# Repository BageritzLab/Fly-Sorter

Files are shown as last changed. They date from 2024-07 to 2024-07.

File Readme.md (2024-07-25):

# Fly Sorter
---
| | |
|-|-|
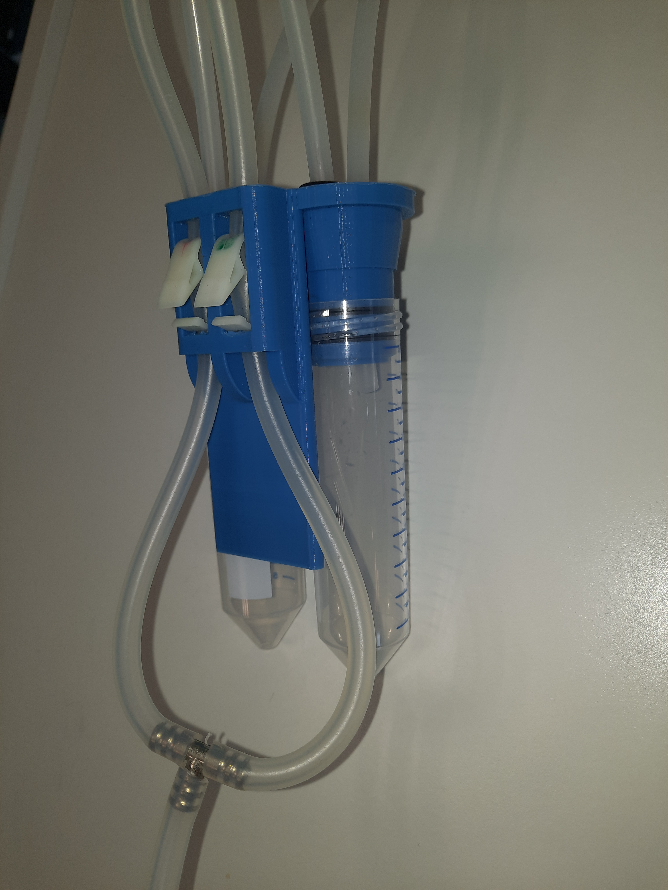
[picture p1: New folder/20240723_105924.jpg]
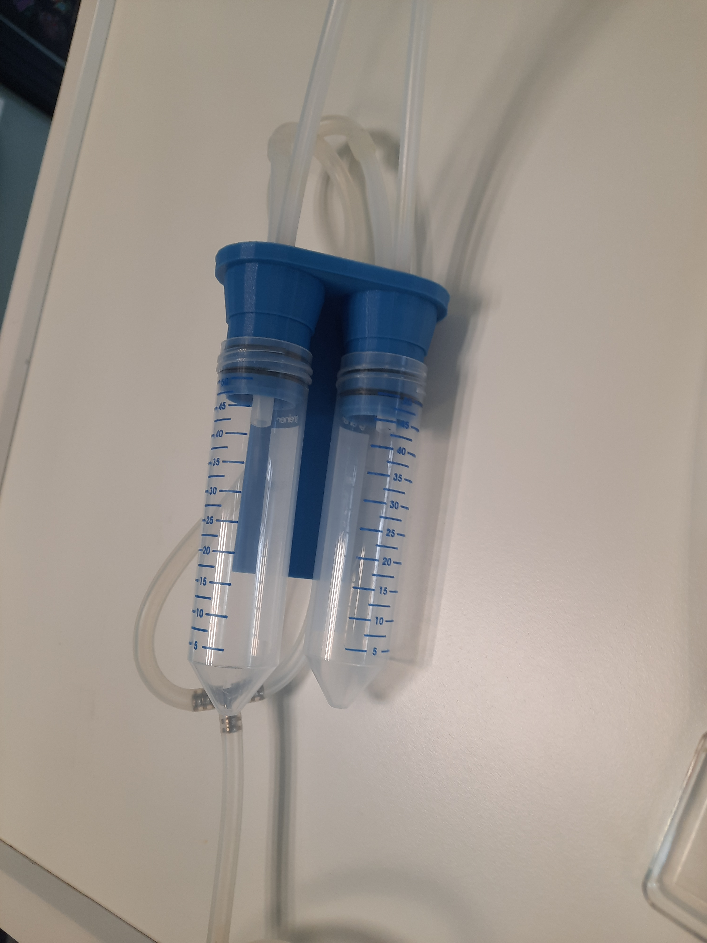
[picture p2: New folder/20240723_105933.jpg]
|| |
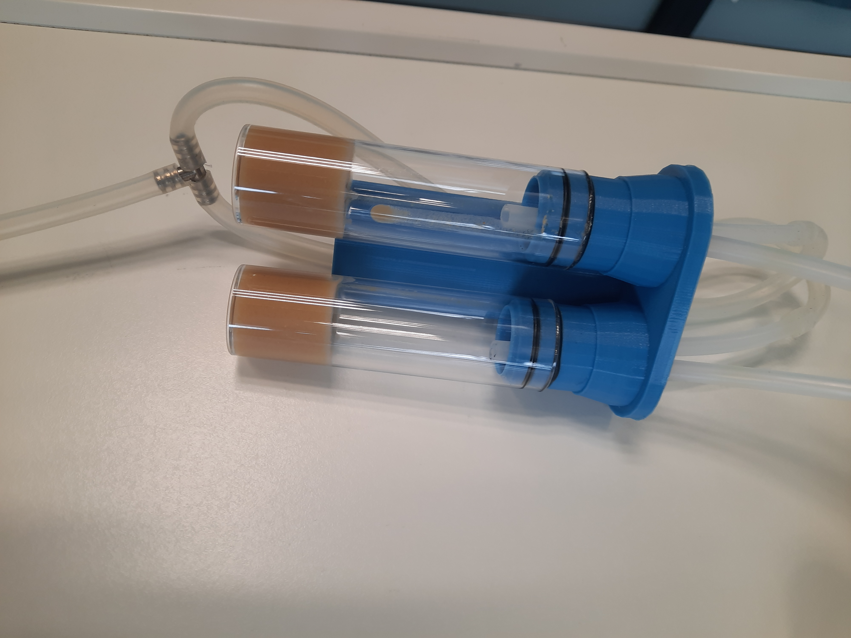
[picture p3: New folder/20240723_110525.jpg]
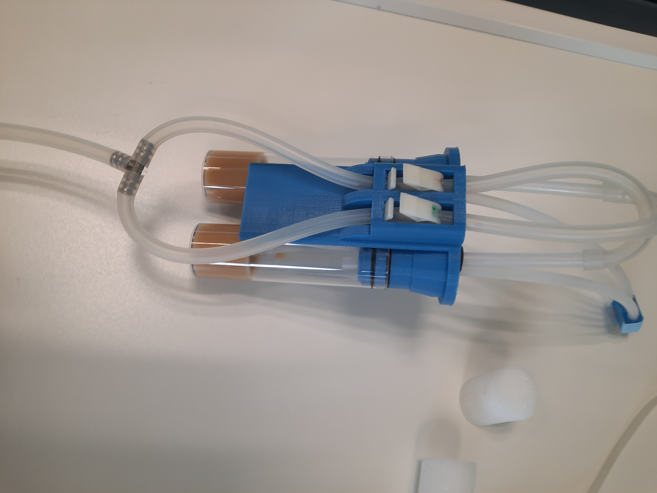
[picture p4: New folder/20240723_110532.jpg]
|||

This is the hand-held Fly Sorter which increases the speed with which *Drosophila* flies can be sorted (e.g. into male and female or by phenotype).

There are two versions of the Fly Sorter:
1. A Quick build that can be made using basic components that can be used with 50 ml Falcon tubes.
2. A 3D printable version that can be used for 50 ml Falcon tubes and standard Laboratpry Fly Vials

Please see the [Building Instructions](https://docs.google.com/document/d/15dwhqNPN-IYihsDtu09y4-i83bKWOhseYIVJSIRqwcc/edit?usp=sharing) for more information.

In our Tests flies that have been sorted 7 consecutive times have not displayed any adverse effects.

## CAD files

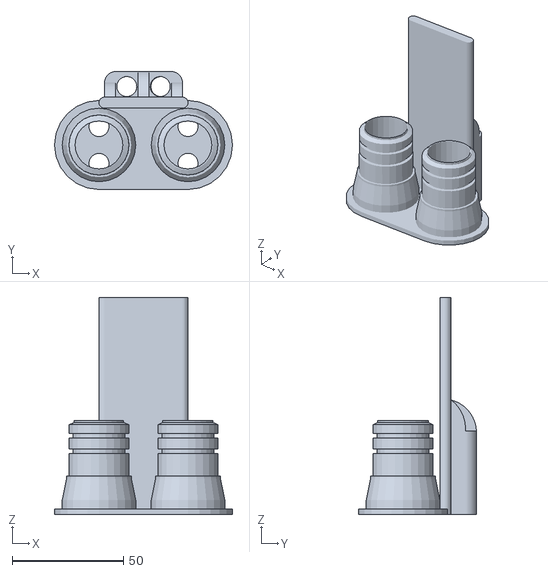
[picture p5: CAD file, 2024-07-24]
Sorter_handle_fly_vials.stl
80.0 x 53.0 x 97.5

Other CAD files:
Sorter_handle_fly_vials.skp

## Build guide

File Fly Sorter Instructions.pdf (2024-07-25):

# Fly Sorter

## Technical Information and Manual

Aim: The Fly Sorter was designed to speed up sorting Drosophila melanogaster flies into categories (e.g. by gender or phenotype) using a handheld vacuum device with 2 chambers.

Quick build (Falcon only) | 1
Material needed: | 1
Building Instructions | 2
3D Printed Device | 6
Material needed: | 6
Build instructions: | 7
How to use the Fly Sorter | 8

# Quick build (Falcon only)

## Material needed:

- 2x 50 ml Falcon Tubes
- 4x silicone cable grommets (inner ø = 6 mm, outer ø = 9 mm)
- A piece of cardboard (~12 cm x ~4 cm)
- Some standard laboratory tape
- T-piece tube connector (ø 5 mm)
- 2x plastic hose clamp
- Drill with 9 mm drill bit Tubing:

- Stiff tubing (inner ø = 4 mm, outer ø = 7 mm)
- 2x ~7 cm
- 2x ~20 cm
- Flexible Tubing (ø = 4 mm, outer ø = 7 mm)
- 2x ~25 cm
- A longer piece to connect to the vacuum

## Building Instructions

1. Drill 2 holes into each of the Falcon Tube caps

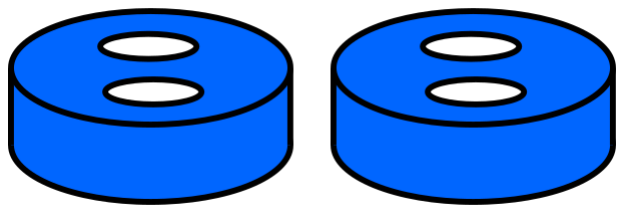
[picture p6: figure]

2. Add the cable grommets into the holes

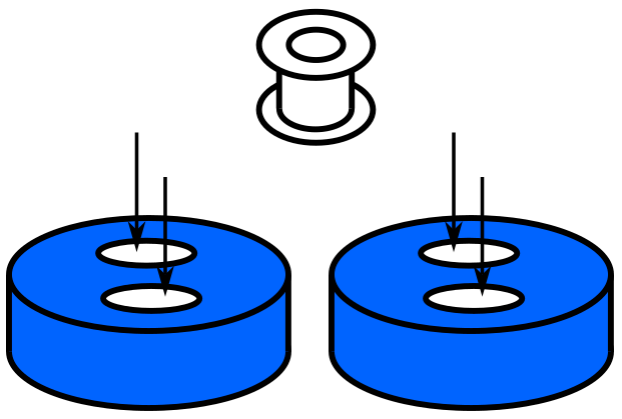
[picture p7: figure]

3. Use tape to fix the lids to each other

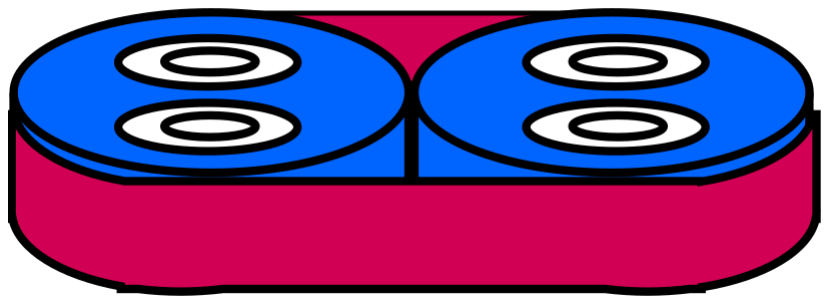
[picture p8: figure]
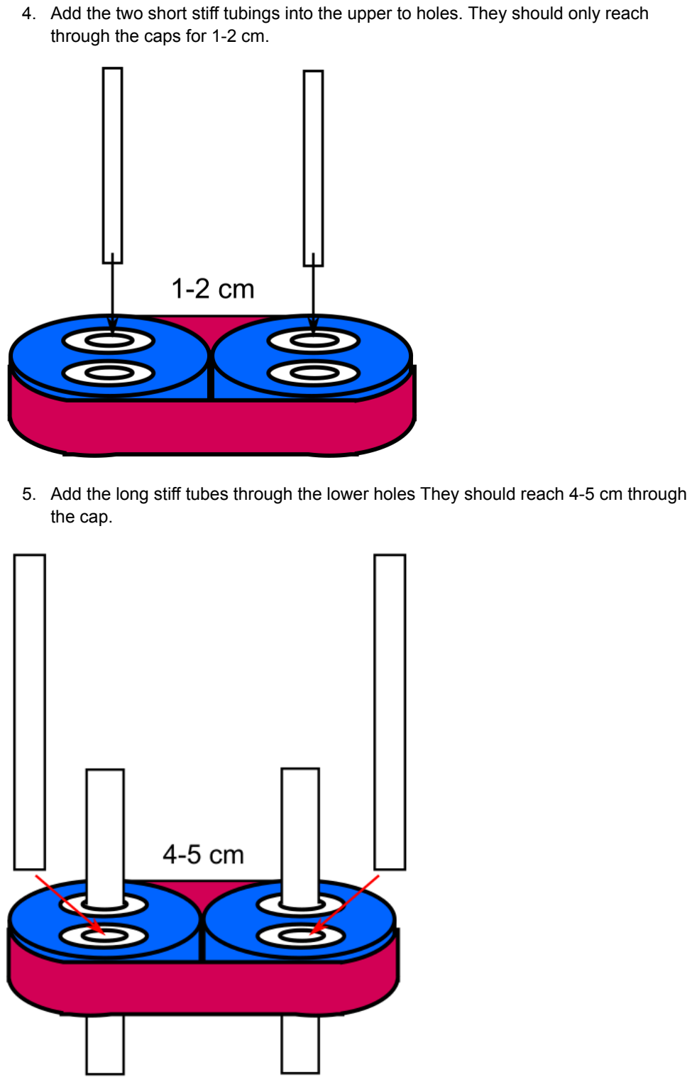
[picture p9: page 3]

4. Add the two short stiff tubings into the upper to holes. They should only reach through the caps for 1-2 cm.
5. Add the long stiff tubes through the lower holes They should reach 4-5 cm through the cap.

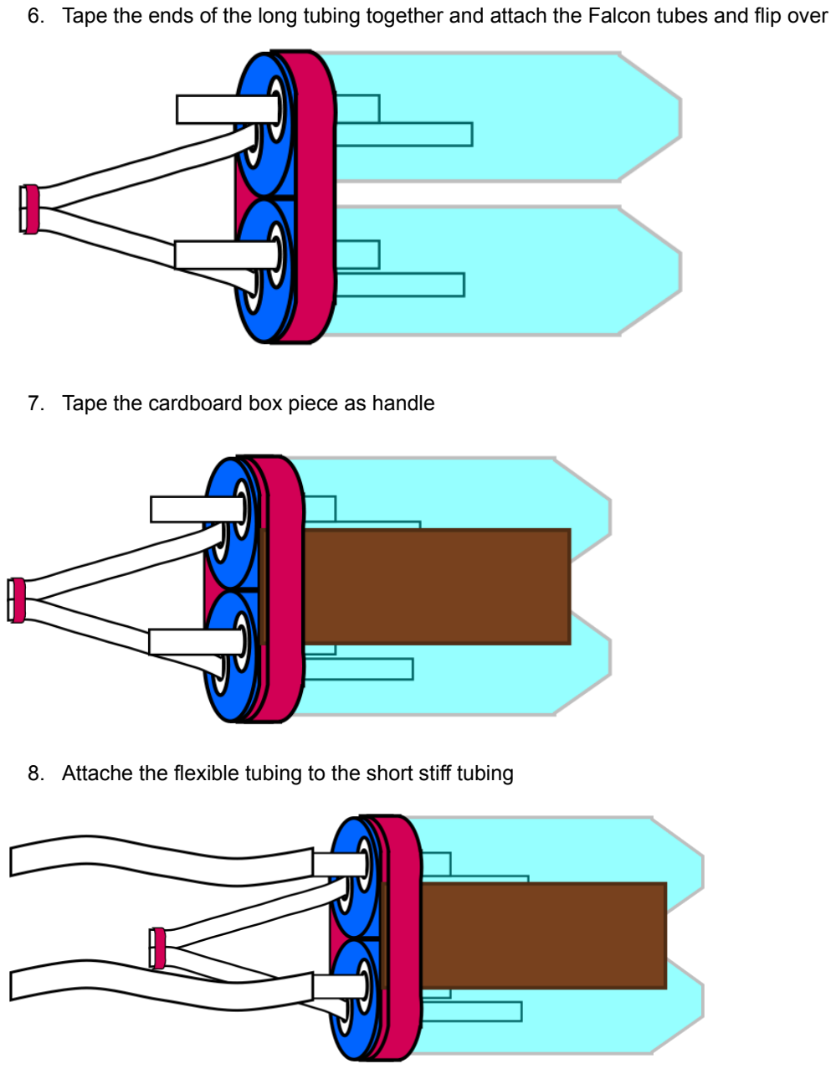
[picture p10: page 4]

6. Tape the ends of the long tubing together and attach the Falcon tubes and flip over
7. Tape the cardboard box piece as handle
8. Attache the flexible tubing to the short stiff tubing

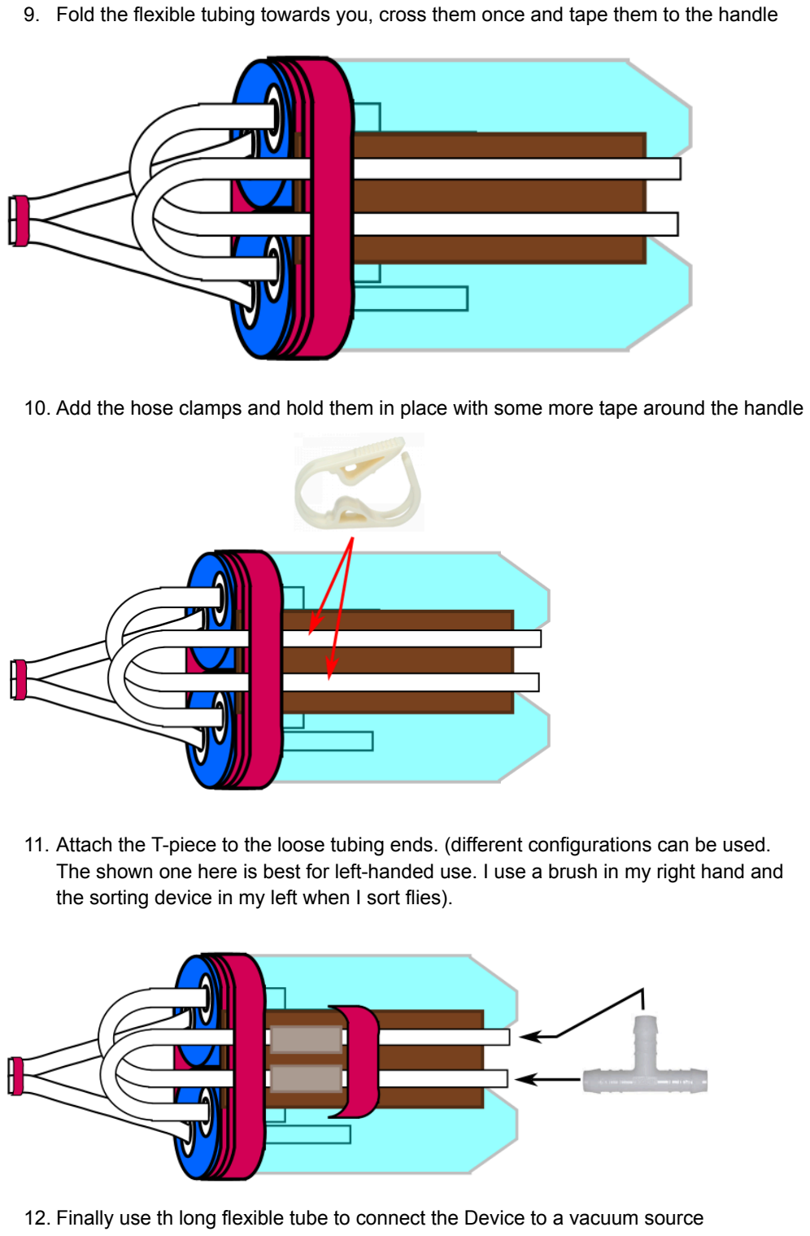
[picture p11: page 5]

9. Fold the flexible tubing towards you, cross them once and tape them to the handle
10. Add the hose clamps and hold them in place with some more tape around the handle
11. Attach the T-piece to the loose tubing ends. (different configurations can be used. The shown one here is best for left-handed use. I use a brush in my right hand and the sorting device in my left when I sort flies).
12. Finally use th long flexible tube to connect the Device to a vacuum source

# 3D Printed Version (Falcons and Fly tubes)

If you have access to a 3D printer I have prepared a 3D printable handle that allows the attachment of Falcon Tubes and standard laboratory fly tubes (inner ø ~27 mm)

## Material needed:

You can download the 3D printer file as .stl from the Bageritz Lab Github page: https://github.com/BageritzLab/Fly-Sorter
I designed the handle in Sketchup Web so an additional .skp is provided.
- 4x silicone cable grommets (inner ø = 6 mm, outer ø = 9 mm)
- T-piece tube connector (ø 5 mm)
- 2x plastic hose clamp
- 4x silicone sealing o-ring (inner ø = 23 mm, outer ø = 27 mm, 2 mm width) Tubing:
- Stiff tubing (inner ø = 4 mm, outer ø = 7 mm)
- 2x ~7 cm
- 2x ~20 cm
- Flexible Tubing (ø = 4 mm, outer ø = 7 mm)
- 2x ~25 cm
- A longer piece to connect to the vacuum

## Build instructions:

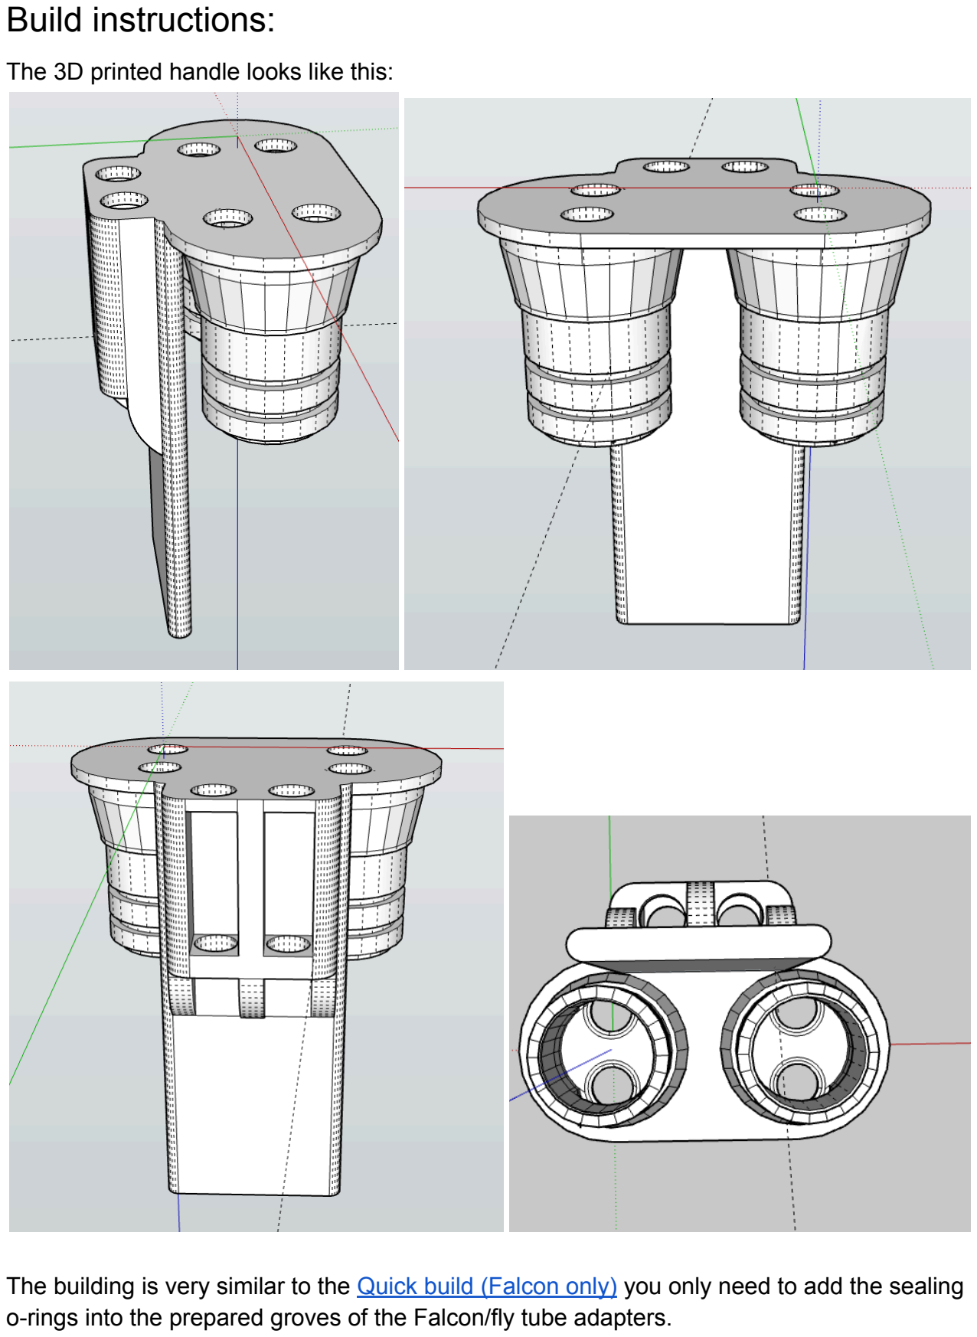
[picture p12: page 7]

The 3D printed handle looks like this:

The building is very similar to the Quick build (Falcon only) you only need to add the sealing o-rings into the prepared groves of the Falcon/fly tube adapters.

# How to use the Fly Sorter

General Use:
1. Attach the Fly Sorter to a vacuum source.
2. (Standby Mode) Adjust the vacuum to the point that a fly that is placed directly in front of the entry is not sucked in but a fly that is already inside of the tubing gets sucked into the collection vial.
(This is important to prevent sucking flies into the wrong vial by accident.)

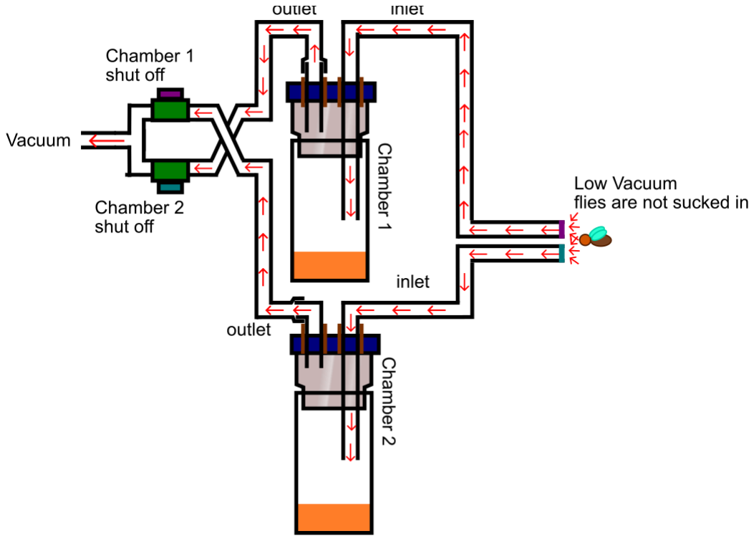
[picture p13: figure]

3. (Active Mode) If you now press the right hose clamp the left collection tube gets shut off and the vacuum in the right collection tube increases to the point were a fly gets sucked into the collection vial and vice versa.

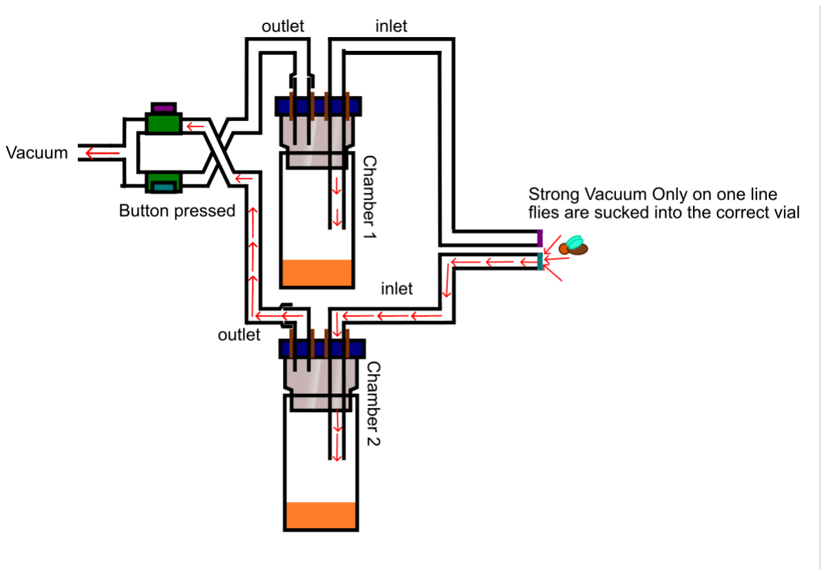
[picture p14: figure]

## Sorting Flies in practice:

I put the flies onto a CO2 pad to anesthezise them. Them I use a bush in the right hand to investigate the flies (decide if they are male of female). The Fly Sorter is held in Standby Mode in the left hand. When we have identified a fly I switch to active Mode by pressing the appropriate button and holding the entry point close to the fly so it is sucked up. This way the CO2 time for the flies is minimized.

Alternatively, you can sort the flies into males and females and put them into distinct piles on the CO2 pad. Then use the Fly Sorter in Active Mode to collect the whole pile.

# Words of caution:

It is possible that eggs get stuck to the tubing and remain there until being dislodged by a following fly. Therefore , there is a risk of contamination. If you are using specific strains that you need to keep separate make sure to rinse the tubing with ethanol/water, and completely dry them.
Alternatively use a new fly sorting setup for each clonal line.

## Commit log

2024-07-23 Adds the sorter handles for fly tubes
    [Sorter_handle_fly_vials.skp, Sorter_handle_fly_vials.stl]
2024-07-24 smaller radus holes
    [Sorter_handle_fly_vials.skp, Sorter_handle_fly_vials.stl]
